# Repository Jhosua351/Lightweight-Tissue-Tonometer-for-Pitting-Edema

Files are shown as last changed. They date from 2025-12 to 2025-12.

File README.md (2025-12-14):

# Lightweight Tissue Tonometer for Detecting Pitting Edema

This repository contains the source code, calibration scripts, and supporting documentation for a capstone project at **Case Western Reserve University**: the design and implementation of a lightweight tissue tonometer device for detecting and classifying **pitting edema**.

---

## Overview
Pitting edema is a clinical symptom characterized by swelling and indentation of tissue due to fluid accumulation. Current diagnostic methods are subjective, relying on visual inspection and manual grading.  
This project introduces the foundation for a future **feedback-controlled tonometer** device that applies a known force and measures tissue displacement, enabling **objective, standardized diagnosis**.

---

## Subsystems
The device integrates three primary subsystems:

- **Force Sensing**  
  - Custom capacitive sensor using penny plates.  
  - FDC1004 capacitance-to-digital converter.  
  - Digital Butterworth low-pass filter for noise reduction.

- **Displacement Sensing**  
  - TCND5000 infrared photodiode sensor.  
  - Exponential low-pass filter for smoothing.  
  - Calibration script converts ADC values to displacement (mm).

- **Pressure Actuation**  
  - Pneumatic bellow system driven by syringe pump.  
  - Designed to apply ~9 N of controlled force.  
  - Displacement range: 6–10 cm.

---
## Repository Contents
- `Sensor-Code/`  
  - `fdc1004_calibration.ino` → Arduino script for force sensor calibration  
  - `tcnd5000_calibration.ino` → Arduino script for displacement sensor calibration  

- `Report/`  
  - `Lightweight Tissue Tonometer For Detecting Pitting Edema Technical Report.pdf` → Final technical report  

- `PCB Files/`  
  - Contains Version 1 and Version 2 PCB layouts and schematics  

- `Capacitive-Force-Sensor-Design/`  
  - Mechanical design files for the capacitive force sensor  

- `Bellow Design/`  
  - `V1/` → First iteration of bellow mold and design  
  - `V2/` → Second iteration with improved flexibility and displacement  

- `Air-Intake-Plus-Clear-Plate-Design/`  
  - Mechanical design of the air intake and clear acrylic plate    

---

## Features
- Sensor calibration with **digital filtering** (Butterworth + exponential smoothing).  
- Conversion of raw ADC values into **voltage and displacement measurements**.  
- Classification of pitting edema into **four clinical grades** based on indentation depth.  
- Debug output for plotting and verification.  

---

## Clinical Grading Scale
| Grade | Indentation Depth |
|-------|------------------|
| 1+    | < 2 mm |
| 2+    | 2–4 mm |
| 3+    | 4–6 mm |
| 4+    | 6–8 mm |

---

## PCB Versions
Two iterations of the printed circuit board (PCB) were developed during the project:

- **Version 1**  
  - Incorporated a motor driver to enable future integration of feedback control.  
  - Layout was less optimized, leading to challenges with signal stability and trace routing.  

- **Version 2**  
  - Motor driver was removed to simplify design and improve tracing.  
  - Enhanced connections for the FDC1004, TCND5000, and supporting components.  
  - More compact and reliable layout.  

Future students should build upon Version 2, but consider further improvements in **shielding** to prepare the design for clinical-grade testing.

---

## Bellow Versions
Multiple versions of the pneumatic bellow were designed and tested:

- **Version 1**  
  - Cast in Dragon Skin 20A silicone rubber.  
  - Wall thickness of 3 mm, triangular folds.  
  - Achieved ~8 mm displacement, below the target of 12 mm.  

- **Version 2**  
  - Reduced wall thickness to 2.5 mm for greater flexibility.  
  - Added a fourth fold to increase expansion area.  
  - Material switched to Silicone Shore 0030 for improved compliance.  
  - Achieved closer to the target displacement range.  

Future students should explore **harder and stiffer silicone materials** to ensure the bellow holds stable under pressure while still achieving the required displacement.

---

## Recommendations for Future Work
- **Electronics**:  
  - Explore PCB miniaturization for wearable applications.    
  - Improve shielding to reduce environmental noise in capacitance measurements.  
  - Investigate a more precise **IR displacement sensor**, since the current TCND5000 loses accuracy beyond ~15 mm.  
    - Note: The sensor begins measuring at ~50 mm due to the combined height of the bellow and acrylic plate, limiting precision.  
  - Improve the **capacitive force sensor design**:  
    - Consider dielectric material between plates.  
    - Add shielding (e.g., enclosing box) to reduce interference from external capacitance sources such as nearby human bodies.
    - Improve shilding on the coaxial wire.  

- **Mechanical Design**:  
  - Refine bellow molds for consistent wall thickness.  
  - Use stiffer silicone materials to improve stability under pressure.
  - Cast a bellow that is black or a darker color to reduce light environmental noise in the IR sensor.   

- **Software**:  
  - Implement closed-loop feedback control for force and displacement.  
  - Add rebound-time measurement to align with full clinical grading standards.    

---

## Getting Started
1. Clone this repository:
   ```bash
   git clone https://github.com/Jhosua351/lightweight-tissue-tonometer.git

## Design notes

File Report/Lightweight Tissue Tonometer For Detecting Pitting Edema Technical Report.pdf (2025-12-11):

### Lightweight Tissue Tonometer Device for Detecting Pitting Edema

Jago Dorn

1,2
(jpd101) Lauren Hong

1
(syh26) Connor Kissack

1
(cak173) Jhosua Oajaca

1,2
(jao101)

Technical Advisor: Dr. Zonghe Chua, Assistant Professor, Department of Electrical, Computer, and Systems Engineering, Case School of Engineering

Instructor: Dr. Vira Chankong

Submitted for ECSE 398 in partial fulfillment for the degree of Bachelor of Science of

Electrical Engineering

1
| Systems & Control Engineering

2

Case Western Reserve University

Fall 2025

### Academic Integrity Policy

All students in this course are expected to adhere to the University standards of academic integrity. Cheating, plagiarism, misrepresentation, and other forms of academic dishonesty will not be tolerated. This includes, but is not limited to, consulting with another person during an exam, turning in written work that was prepared by someone other than you, making minor modifications to the work of someone else and turning it in as your own, or engaging in misrepresentation in seeking a postponement or extension. Ignorance will not be accepted as an excuse. If you are not sure whether something you plan to submit would be considered either cheating or plagiarism, it is your responsibility to ask for clarification. For complete information, please go to https://students.case.edu/community/conduct/aiboard/policy.html.

The individual(s) submitting this document affirm compliance with the above statement

# Lauren Hong Connor Kissack Jhosua Oajaca

[This page intentionally left blank]

### Executive Summary

Pitting edema is a symptom of the accumulation of intercellular fluid in tissue cells that results from an increase in interstitial fluid, characterized by swelling of tissues and formation of an indentation wherever pressure is applied to the skin. While early detection is critical because it indicates underlying heart, liver, or kidney issues, current diagnostic methods are subjective, relying solely on a clinician’s visual assessment and grading of the skin indentation and rebound time. To address the lack of standardization, potential misclassification of severity, and delayed diagnosis, we designed a feedback-controlled tonometer capable of applying a known force and precisely measuring skin displacement and the normal force exerted by the skin on the device. Our methodology integrates three primary subsystems: (1) a capacitive force sensor to measure the force applied to the skin, utilizing two isolated copper plates and a capacitance-to-digital converter (FDC1004) to quantify the normal force; (2) an infrared displacement sensor (TCND5000) to measure the depth of the pit formed; and (3) a pneumatic actuator that uses a syringe pump, motor, and motor driver to regulate the pressure in a silicone bellow to apply constant indentation. We expect the device to apply a controlled force of approximately 10 N and measure skin indentation. We expect the prototype to deliver consistent, precise performance across its subsystems. The device is designed to measure internal actuation displacement over a range of 0–12 mm. Additionally, the device will record and process data sufficient to classify pitting edema into the four standard clinical categories, thereby laying the groundwork for objective, standardized diagnoses.

[This page intentionally left blank]

### Table of Contents

[This page intentionally left blank]

### Problem Statement

Pitting edema is a symptom of the accumulation of intercellular fluid in tissue cells that results from an increase in interstitial fluid, characterized by swelling of tissues and formation of an indentation wherever pressure is applied to the skin. While early detection is critical because it indicates underlying heart, liver, or kidney issues, current diagnostic methods are subjective, relying solely on a clinician’s visual assessment and grading of the skin indentation and rebound time. To address the lack of standardization, potential misclassification of severity, and delayed diagnosis, we designed a tonometer capable of applying a force and precisely measuring skin displacement and the normal force exerted by the skin on the device. This system would allow either healthcare professionals or researchers to collect data, helping them create a validated grading system. Future iterations of this system could also allow patients to measure the extent of their pitting edema, encouraging timely care-seeking behaviors that could support early diagnosis or better chronic disease management.

The overall goal of this project is to design a fully functional tonometer device that applies and measures force and displacement by pressing into the patient’s tissue (typically on the forearm or calf), serving as a proof-of-concept design to provide clinicians with reliable, objective measurements to support the diagnosis and monitoring of pitting edema. To achieve this, we will design and implement subsystems for force sensing, displacement sensing, and actuation/pressurization.

A relatively long search for relevant studies and papers returned no devices that used similar methods to measure pitting edema. The most relevant paper we found was “Quantitative measurement of pitting edema with a novel edema ruler” [1], in which the team designed and 3D-printed a handheld tool to measure the depth of a pit created by manually applied pressure, which could then be used to help physicians in subjectively deciding an edema grade level for the patient. There has been some discussion of the lack of standardization in grading pitting edema [2], suggesting a common interest in a solution like the one we designed in our project. Similar circulatory issues can be detected with the peripheral arterial tonometry, a non-invasive test that assesses circulation by measuring changes in blood flow and arterial function [3]. This shows that using objective, sensor-based measurements has already improved the diagnosis of related issues, highlighting how our tonometer could help make edema assessments more consistent.

### Purpose, Goals, & Objectives

The purpose of this project is to develop a prototype diagnostic tonometer device that applies force to the skin at various body locations to measure tissue displacement and objectively assess the severity of pitting edema. With this device, clinicians would be able to quantify the applied force and the resulting tissue displacement, thereby standardizing the diagnostic method for edema.

This project supports the organizational objectives of creating a standardized diagnostic method to improve accuracy and consistency, and of creating a final wearable device ready for marketing to clinicians and, in the future, patients who want to self-assess at home. The business problem being addressed is the potential delay in diagnosis, which could lead to misclassification of disease severity and, in turn, increase care costs. This project has a high priority because this device can improve both clinical decision-making and self-monitoring for at-risk patients at home. In the long term, this device can improve chronic disease management and support preventive and remote monitoring.

The three main aspects of the project that are necessary to support the desired functionalities are
(1) force sensing, (2) displacement sensing, and (3) pressure actuation. The force sensor records force data that may help researchers determine whether the amount of force applied is a variable that can guide methods for grading pitting edema. It also helps as a safety measure by creating a stopping point for the applied pressure, ensuring that reasonable pressure is applied so the patient does not get hurt. In future developments of this device, the force sensor will help create a feedback control system that applies the force needed to maintain constant tissue displacement, thereby helping determine the normal force exerted by the skin on the device. The displacement sensor measures the amount of tissue displacement created by the device's applied force, which is the main functionality of our device. The pressure actuation subsystem generates the pressure that induces indentation in the patient’s skin.

Dr. Chua’s team aims to develop a wearable device that precisely measures and categorizes pitting edema with minimal involvement from healthcare professionals. Before beginning our project, the device was at a Tech Readiness level of two (“Technology Conceptualized”) [4], with a timeline of 5 to 7 years before it could be implemented in a healthcare setting. Our project team aimed to demonstrate key elements in a laboratory environment that would indicate progression to a Tech Readiness level four (“Partial Scale Prototype & Modeling”) [4]. Our project is a prototype subsystem that will provide foundational data and establish a developmental framework for Dr. Chua’s team.

### Background & Context

Pitting edema is usually checked using a pretty straightforward method: a doctor presses a finger into the patient’s skin, usually on the forearm or calf, and watches how deep the dent goes and how long it takes for the skin to bounce back. This “finger method” [5] is standard, but it is pretty subjective, meaning it depends heavily on the doctor's opinion of how bottomless the pit is and how quickly it rebounds. Because of this, different practitioners can end up grading it inconsistently, which can slow down the diagnosis of serious issues like heart problems, kidney trouble, or liver disease.

To address this inconsistency, researchers have explored more precise methods. One notable innovation is the edema ruler [1], a small device made to measure the depth of the pit more accurately. While the ruler gives a specific number for the indentation's depth, it still relies on manual pressure and does not account for how quickly the skin rebounds or how evenly the pressure is applied. So, even though it is a step forward in accuracy compared to the finger method, it is not perfect for eliminating variability in assessment.

In practice, pitting edema is typically classified into four standard grades based on how deep the indentation is:

Table 1 - Pitting Edema Grade Scale [7]

Grade | Indentation Depth | Rebound Time
1+ | < 2 mm | Immediately
2+ | 2 - 4 mm | < 15 seconds
3+ | 4 - 6 mm | < 60 seconds
4+ | 6 - 8 mm | 2 − 3 minutes

While rebound time is important for identifying and classifying pitting, it was out of scope for this project. We hope that, with future updates using feedback-controlled actuation, we can add a rebound time to create a more rounded diagnostic tool.

By placing our work alongside existing diagnostic methods (such as the finger method and the edema ruler), the clinical grading standards, and the technical challenges of sensor development, this project shows both the need for and the potential of a standardized, quantitative tonometer for assessing pitting edema.

### Success Criteria

The project will be a success if the following criteria are met or exceeded:
- The device can measure internal actuation displacement with an uncertainty of ±1 millimeter.
- The device can measure force at the end effector with an uncertainty of 10%.
- The device end-effector can detect contact with human skin within 0.5 seconds, with at least 1 newton of force applied.

- The device can extend and retract the end effector by at least 8mm at a frequency of at least 0.25 Hz.
- The device can record and share data that enables the classification of pitting edema into the four categories. The categories are defined by the pit depth: < 2 mm, 2-4mm, 4-6mm, and > 6 mm [7].
- The device complies with the standards listed below.

The constraint of measuring internal actuation displacement with an uncertainty of ±1 millimeter is most impactful to our device design, as it is our primary means of measuring pitting edema. In the most severe cases, pitting edema may produce depressions of around 8 millimeters, meaning that even small measurement errors could alter the assigned edema grade. Achieving ±1 millimeter uncertainty constrains the selection of sensors, mechanical tolerances of the pressure actuation subsystem, and the stiffness of the different materials used (silicone of the bellow, flexures of force capacitors, etc). It also influences the calibration process, necessitating the removal of noise or drift so that the measurements reflect close to true tissue indentation. This success criterion drove both mechanical and electrical design decisions and ultimately ensured the clinical meaningfulness of the device.

The constraint of measuring force with an uncertainty of 10% at the end effector is also meaningful to our device design, as it records the load applied to the skin, providing researchers with data that may show whether the applied force is a reliable parameter for guiding clinical grading pitting edema. It also functions as a safety mechanism by defining an upper limit on applied pressure, ensuring the device cannot exert excessive force that may cause patient discomfort or injury. This is one necessary part for future FDA approvals, as safety is a priority. In future iterations, accurate force measurement will be essential for implementing a closed-loop feedback controller that can modulate the actuation pressure to maintain a constant tissue displacement. This will allow the system to determine the normal force exerted by the skin against the device, another key parameter of interest. Because force interacts directly with the displacement-sensing and pressure-actuation subsystems, a 10% uncertainty constraint places strict requirements on sensor selection, mechanical design of the capacitor, and calibration, ensuring that the measured force reflects close to the true applied force and normal force rather than system noise or environmental noise.

The success criteria that the device should extend and retract the end effector by at least 8 millimeters at a minimum frequency of 0.25 Hz directly influences the design of the pressure-actuation subsystem. Because displacement is our primary measurement, the actuator must be capable of producing sufficient stroke length to replicate the full range of clinically relevant pitting-edema levels of depth. Meeting this displacement requirement ensures that we can reliably induce measurable pits across the full spectrum of edema severity. The frequency requirement of 0.25 Hz also constraints the performance of the actuator so that the system can complete a full indentation-release cycle every four seconds. These constraints affect the selection of the actuation mechanism, the stiffness and response characteristics of the bellow, and the sizing and control strategy of the pneumatic subsystem. They also shape the decisions in making the overall mechanical design to ensure repeatable motion and minimal latency.

### Technical Constraints

The accuracy of the force and displacement sensing portions of the device must remain within clinically acceptable tolerances, as the differences in displacement and force pushback from the skin are minute, and the degrees of pitting edema can differ by tiny increments. To provide meaningful diagnostic value, we must balance cost and sensor precision, and place strict requirements on sensor selection and calibration methods.

Another constraint during the prototype phase is size. To mimic current manual depression methods on the patient’s skin, the device needs a pressure tip no larger than a thumb, or about 2 cm in diameter. The rest of the device needs to be compact enough to be made into a wearable device that securely fits on a person’s limbs. Future iterations will need to consider shrinking the device to meet the size specifications required to make this into a wearable device.

Safety constraints should also be considered, as we want to ensure that safety restrictions are in place to prevent excessive pressure on the patient.

### Standards

Our project will follow a set of standards to make sure the device is safe, reliable, and easy to integrate with other systems. On the regulatory side, we’ll meet the FCC requirements under Title 47, Part 15 (Sections 15.23 and 15.5), which cover electronic emissions and interference. For the hardware, we’ll use IEC 60320-1 for electrical connections and IPC-2221B for printed circuit board design (PCB). For communication, we’ll rely on IEEE 1118.1-1990 for microcontroller control buses and the I2C protocol to handle data transfer between subsystems. Since this is a medical-focused project, we’ll also reference ISO/IEEE 11073 standards to keep our device aligned with healthcare communication practices and patient safety.

1) Generic Standard on Printed Board Design, IPC-2221B, IPC, Bannockburn, IL, 2012. [Online]. Available: IPC_2221.pdf (https://www-eng.lbl.gov/~shuman/NEXT/CURRENT_DESIGN/TP/MATERIALS/IPC_2221.pdf)

IPC-2221B, Generic Standard on Printed Board Design, is an industry standard published by IPC that provides the design principles and requirements for printed circuit boards (PCBs). It covers material selection, conductor spacing, thermal management, mechanical layout, and electrical performance considerations. Its purpose is to ensure manufacturability and safety across PCB applications by establishing design rules that can be adapted to different technologies.

1) Radio Frequency Devices, Title 47 CFR Part 15, Federal Communications Commission,
Washington, | D.C., | 2023. | [Online]. | Available:
https://www.ecfr.gov/current/title-47/part-15

Under Title 47, Part 15 of the FCC rules, Section 15.23 allows individuals to build and operate low-power radio frequency devices for personal use without formal equipment authorization. Provided no more than five units are made, and they do not cause harmful interference. Section 15.5 sets out the operating conditions for all Part 15 devices. They must not cause harmful interference to licensed radio services, must accept any interference received, and must stop if ordered by the FCC.

2) Universal Serial Bus Type-C Cable and Connector Specification, Release 2.4, USB 3.0
Promoter | Group, | Oct. | 2024. | [Online]. | Available:
https://www.usb.org/document-library/usb-type-cr-cable-and-connector-specification-rele ase-24 (https://www.usb.org/document-library/usb-type-cr-cable-and-connector-specification-release-24)

The USB Type-C Cable and Connector Specification Release 2.4 provides the newest framework for ensuring safety performance across devices that adopt the standard. This release refines definitions for cable assemblies, connector requirements, and extended power delivery. It introduces updated compliance requirements for USB4 Gen4 and liquid corrosion mitigation and alternate modes. For engineers and system designers, this serves as a reference for implementing Type-C technology in devices.

3) IEEE Standard for Microcontroller System Bus, IEEE Standard 1118.1-1990, 1990. [Online]. Available: https://ieeexplore.ieee.org/document/159173

The IEEE 1118.1-1990 standard defines the specifications for microcontroller control buses, providing a uniform method for communication between microcontrollers and peripheral devices. It establishes electrical, timing, and protocol requirements for data transfer, device interoperability, and control in embedded systems. By standardizing bus operations, IEEE 1118.1-1990 helps reduce design complexity, promotes hardware compatibility, and supports scalable system development.

4) Solderability Tests for Component Leads, Terminations, Lugs, Terminals and Wires, Joint standard, EIA/IPC/JEDEC J-STD-002E, IPC, EIA, and JEDEC, Nov. 2017. [Online]. Available:https://webstore.ansi.org/preview-pages/ipc/preview_j-std-002e.pdf?srsltid=AfmBOopS_s9edY3xJrSCdWhQsNor4nRz5zq07qOXc5j1KHITtFKT7D1X (https://webstore.ansi.org/preview-pages/ipc/preview_j-std-002e.pdf)

The J-STD-002E standard provides a methodology for evaluating the solderability of component leads and wires used in electronic assemblies. It establishes visual criteria and force measurement tests. These procedures verify the components maintain acceptable solderability throughout storage and assembly. The standard helps suppliers and users ensure long-term reliability.

5) Reference Designations for Electrical and Electronics Parts and Equipment, ASME Y14.44-2008, The American Society of Mechanical Engineers, Nov. 21, 2008. [Online]. Available:
https://www.intertekinform.com/preview/98393739772.pdf?sku=138813_SAIG_ASME_ASME_2631634&srsltid=AfmBOoqN_DQIZ4u7QUdkdc9FvU-_kXyi-eiCwLqGUh5Ni5 6hMhtX3eZU (https://www.intertekinform.com/preview/98393739772.pdf?sku=138813_SAIG_ASME_ASME_2631634)

This defines a uniform system for reference applied to electronic equipment. It specifies methods for unit numbering so that components are identifiable in documentation. Y14.44 reduces ambiguity in system layouts and supports manufacturing teams.

6) IPC-A-610E: Acceptability of Electronic Assemblies, IPC – Association Connecting
Electronics | Industries, | Apr. | 2010. | [Online]. | Available:
https://datasheet.datasheetarchive.com/originals/crawler/acdi.com/4fa15157e5b81fef1873 e725a900d3e8.pdf (https://datasheet.datasheetarchive.com/originals/crawler/acdi.com/4fa15157e5b81fef1873e725a900d3e8.pdf)

The standard provides criteria for the inspection and quality evaluation of electronic assemblies. It establishes classifications for assemblies. Class 1: general electronic products, Class 2: dedicated service, and Class 3: high-performance.

### Approach & Design Methodology

Our approach uses three main subsystems: Force sensing, displacement sensing, and pressure actuation. We chose this path because it strikes a balance among accuracy, safety, and practicality, while also building on methods that are more reliable than current clinical evaluations.

We felt this was the best direction compared to existing options, such as simple mechanical tonometers, which aren’t very accurate and depend heavily on the clinician. Our approach enables more objective and repeatable results, setting the stage for future improvements to wearable devices.

Force Sensing

While working on our prototype, we ran into familiar measurement issues. At first, we considered using a standard resistive force sensor, but they are often inaccurate, prone to drift, and challenging to customize. To tackle these problems, we decided to design and build our own capacitive force sensor. Since we were on a tight budget, we used two copper pennies from before 1982 as the capacitor plates. While this worked, it came with its own set of challenges: pennies are less conductive than aluminum and are more affected by environmental noise. With a larger budget, we would have substituted the pennies for slices of aluminum rods for the capacitor plates to improve conductivity and reduce sensitivity to noise.

We designed our capacitor using two isolated copper plates. These have a capacitance between them that can be measured using a capacitive-to-digital chip. The plates are mounted on a flexure that compresses when force is applied. These plates were sized appropriately and fixed at a 1.5 mm distance to ensure the reading of a maximum capacitance of 15 pF when applying a maximum force of 10 N. This was done to ensure that the applied force remained within the FDC1004's range, a four-channel capacitive-to-digital converter.

Calibration was another big hurdle. The capacitive sensor was picking up significant external noise, so we implemented a digital low-pass filter, or specifically a first-order Butterworth low-pass filter, to smooth the signal and remove noise.

This filter is defined by its discrete-time transfer function H[z] = | , where | is the

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
−1 ] + ω0

ω0

cutoff frequency and T is the sampling period. And the corresponding difference equation we
s
used to implement this filter is y[k] = ( | | .

2−ω0

T
s
2+ω0

Ts

)y[k − 1] +

ω0

T
s
2+ω0

Ts

x[k] +

| ω0 T s 2+ω0 Ts
x[k − 1]

Even with filtering, some readings were too weak to be useful, so we added an amplifier to boost the signal into a measurable range. While calibrating, we also realized that the flexure holding the pennies was flawed in that the flexure would not rebound fully over time, causing drift in our capacitance measurements. These steps were essential for meeting our accuracy goals, but they really highlight how tough it can be to build reliable biomedical sensors when resources are limited.

Displacement Sensing

To measure skin response, we used a photodiode displacement sensor. This sensor will help us track how far the skin is displaced. This works by measuring the internal displacement of the bellow through emitting and detecting infrared light. By measuring the current generated by the photodiode, we can determine how close the opposite side of the bellow is to the sensor. We chose this method due to its low cost, precision, and ease of integration compared to more bulky or less accurate alternatives.

Pressure Actuation

For the actuation subsystem, we developed a pneumatic bellow to apply controlled pressure in the y-direction. Our first version was inspired by a Soft Robotics project that focused on pneumatic actuators, which we used as a guide for designing the mold and its shape [6]. We made a two-piece mold for the bellow, keeping three main things in mind: wall thickness, folding angle, and fold shape.

For wall thickness, we went with 3 mm after reviewing a research paper on soft-bellow actuators [7]. At 50 kPa, this thickness yielded the best deformation, with a displacement of 14.58 mm. In contrast, a six mm-thick option only provided 5.49 mm of movement [7]. While the original actuator was for a different purpose, the design and pressure factors still worked for what we were trying to do.

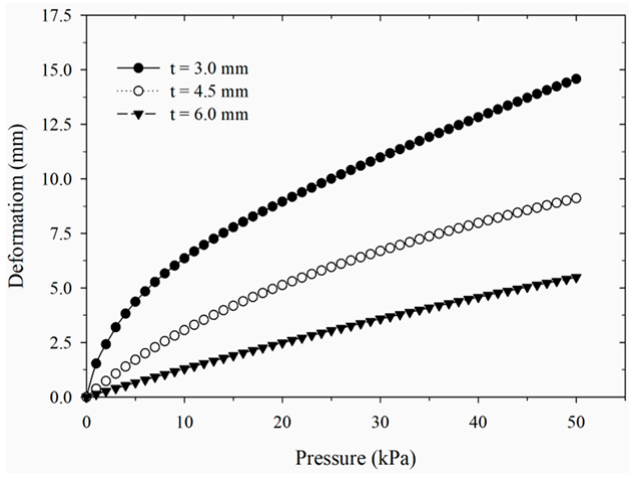
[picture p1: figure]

Figure 1: Simulation result of deformation response under 50 kPa pressure with wall thickness of 3mm [7]

We chose a folding angle of 30° based on the techniques described in the paper on soft bellow actuators and on Dr. Chua’s previous work with mechanical bellow designs [8]. For the fold shapes, we kept it simple with triangular designs, following the guidelines from the Soft Robotics project [7].

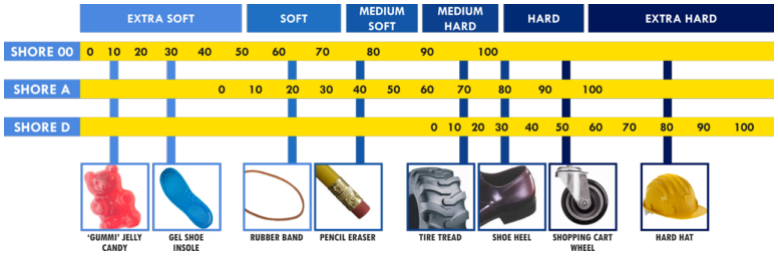
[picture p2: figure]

Figure 2: Silicon Shore Hardness Scales [9]

For the materials, we cast the bellow in Dragon Skin 20A silicone rubber. This was a good choice because it is as flexible as a rubber band, and we thought it would let the bellow expand up to 12 mm, which was our goal. We also used epoxy glue made for silicone to stick the two halves together since we cast it in two parts.

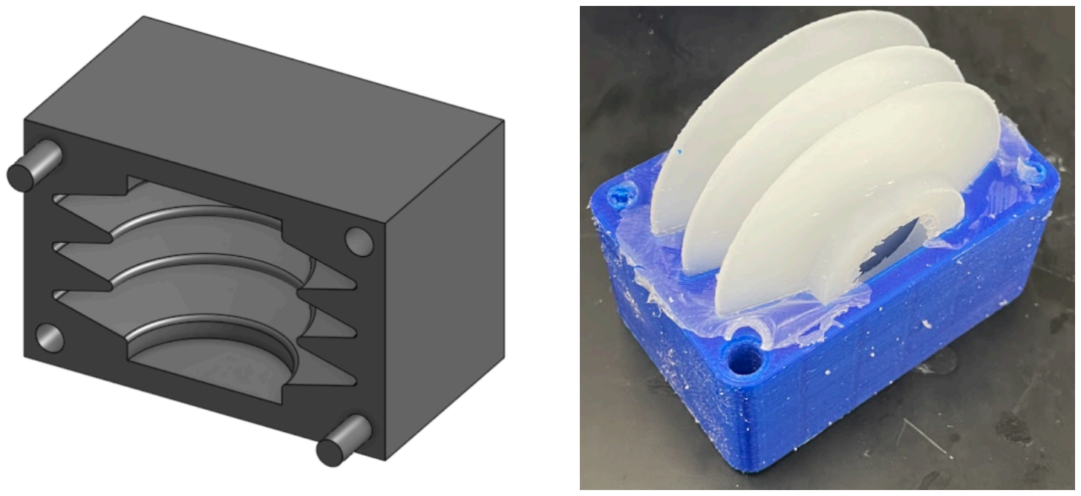
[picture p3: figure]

Figure 3 - Bellow Mold and Cast

Testing it with a syringe showed that our first design did not quite reach the target of 12 mm, expanding only to 8 mm. To fix that, we created a second design with some changes: we added a fourth fold to increase the expansion area, reduced the wall thickness from 3 mm to 2.5 mm for greater flexibility, and switched the material from Dragon Skin 20A to Silicone Shore 0030 for even greater compliance. These tweaks improved the actuator’s performance and helped it get closer to meeting our displacement goals.

Physical Device

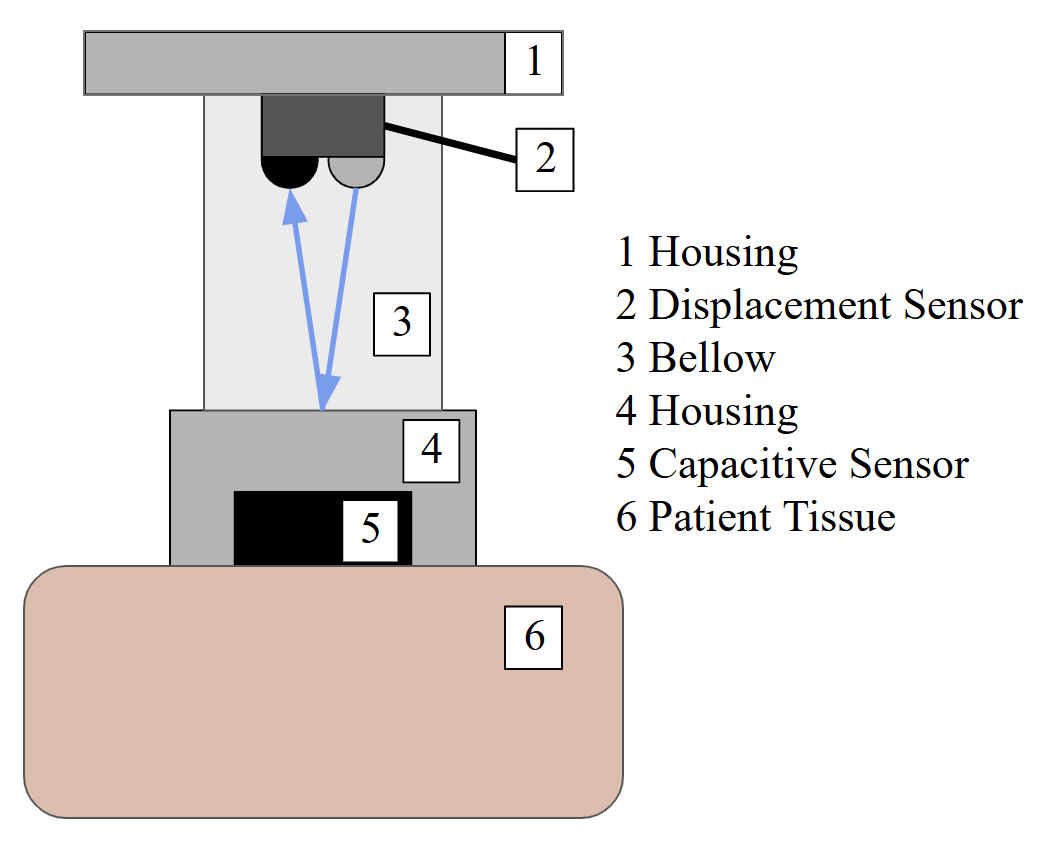
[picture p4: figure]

Figure 4: Hardware Design Overview

Figure 4 shows the design overview and how the device is supposed to work. As the bellow is inflated, the distance between the housings will increase, and this will be read using an infrared emitter and detector sensor circuit. The force of the patient’s tissue against the device will be measured using the capacitive sensor. This way, we can determine whether we are in contact with the patient, whether the tissue is responding in a way consistent with edema, and how deep the tissue has been displaced.

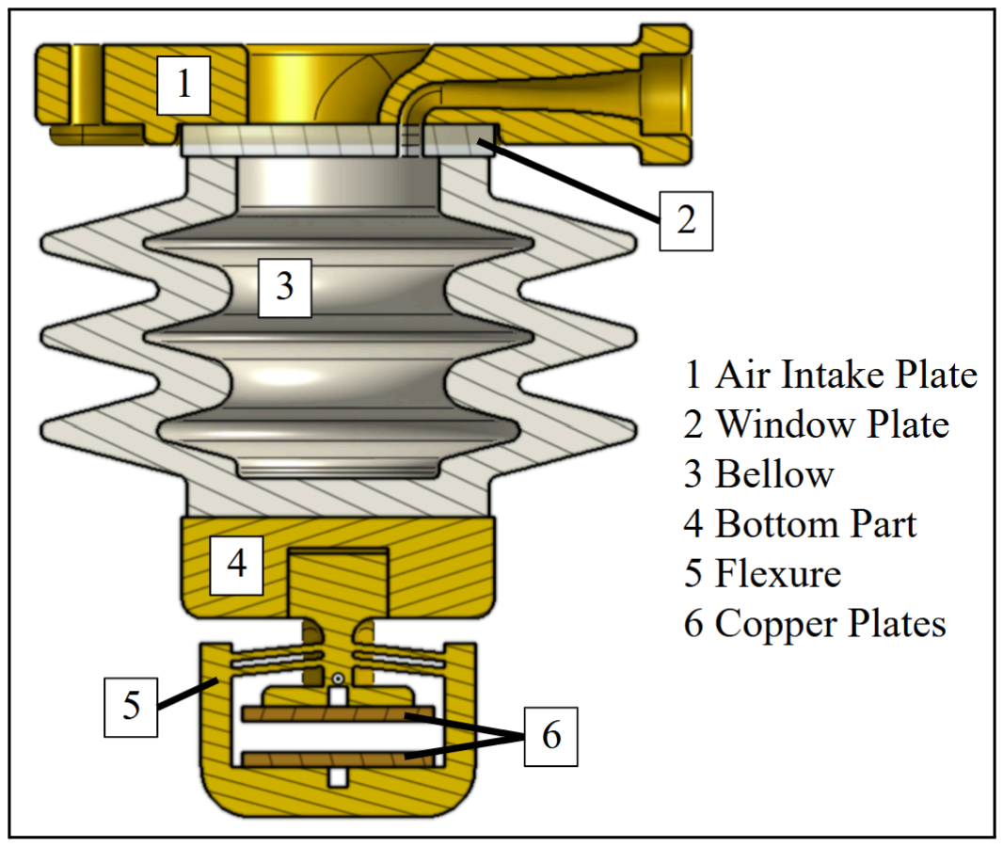
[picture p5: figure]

Figure 5: Physical Computer-Aided Design

The physical design consists mainly of the components listed above. This is in addition to the printed circuit board mounted on the air intake plate, several wires, and the air intake hose. This design was created in Onshape, a computer-aided design (CAD) software.

Circuit Design

Schematics for the displacement sensor, capacitance sensor, and ESP32 pinout and connections were all designed in KiCAD, a circuit design software. Then, these schematics were combined and translated into a printed circuit board layout in KiCAD. The printed circuit board was designed to implement shielding for our capacitive sensor, mitigate environmental noise with two-layer ground fills, and parallel traces to reduce crosstalk.

Alternative Designs

Both the physical and circuit designs had multiple iterations. Shown below are some iterations for each component.

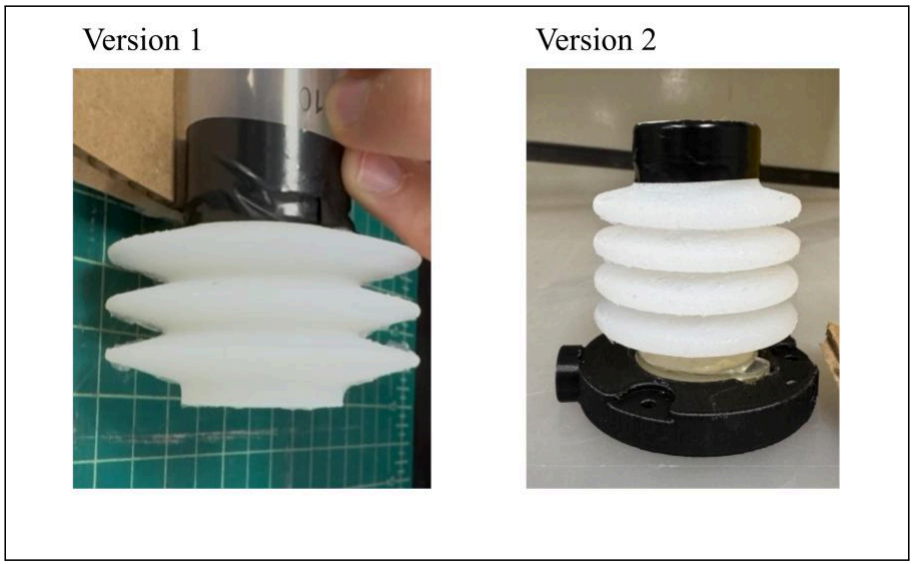
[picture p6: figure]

Figure 6: Bellow Iterations

Bellow version 1 did not have adequate extension when inflated. For this reason, and to create a thicker wall for better adhesion to the top and bottom fixtures, version 2 was created.

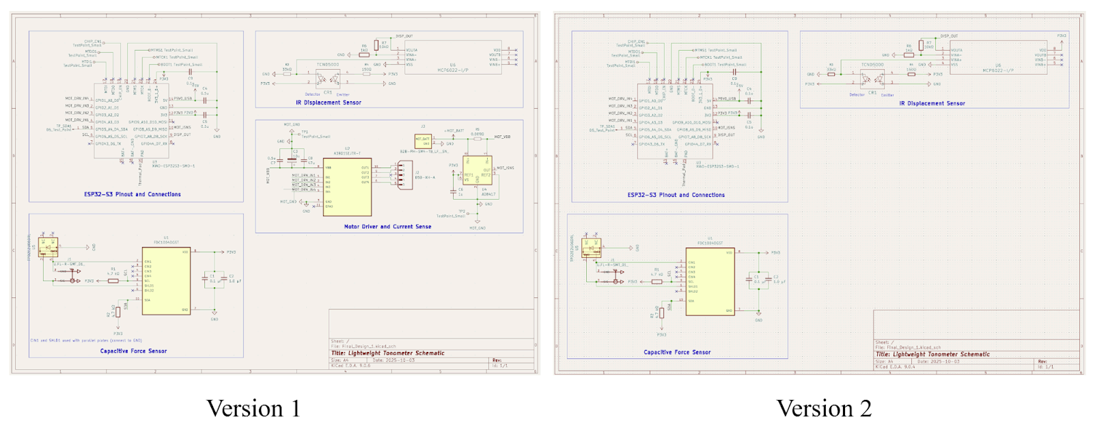
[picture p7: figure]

Figure 7: Schematic Iterations

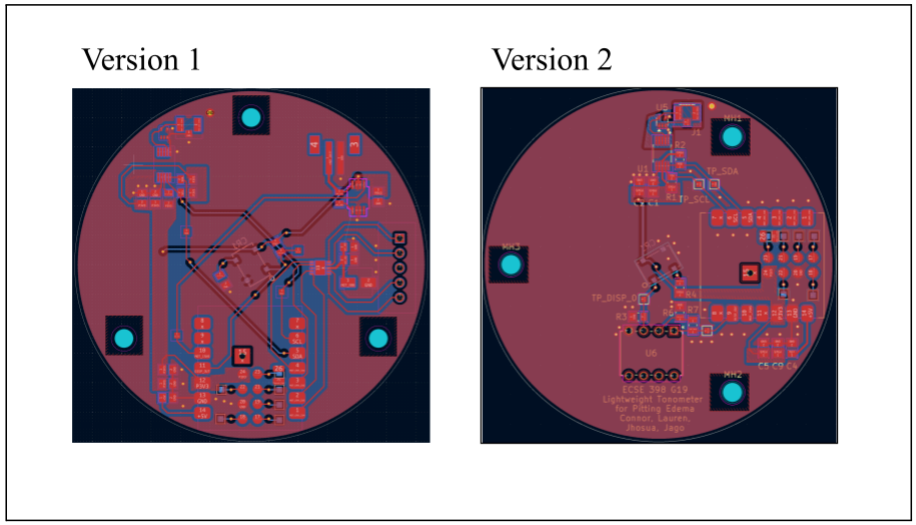
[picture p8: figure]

Figure 7: PCB Iterations

After testing our first PCB, we determined that the displacement sensor did not vary enough to provide accurate data and was highly susceptible to external noise. After troubleshooting and experimentation, we found a solution, implemented it in our second schematic version, and then updated the PCB design. In addition, we removed the current-sense feature and motor-driver connectors, which were used when the project had a broader scope. We also widened the driving-voltage traces and added a through-hole for an operational amplifier to increase gain in the displacement sensor’s output. As a precaution, we also redesigned the capacitance force sensor circuitry to improve I2C connectivity by shortening the SDA and SCL traces, making them as parallel as possible, and ensuring there were no breaks in the ground plane beneath the traces and pins.

By combining these subsystems, we designed a proof-of-concept device that integrates force sensing, displacement measurement, and pneumatic actuation into a single system.

### Verification & Results

Our first criterion was to ensure that our device measures internal actuation displacement with an uncertainty of ±1 millimeter. This was established using the TCND5000 IR sensor, implementing a first-order, digital low-pass Butterworth filter and a moving average function to reduce noise, situating our IR sensor perpendicular to a wall, and using a caliper to corroborate distances to voltage readings with the sensor. As a result, we decided to set the cutoff frequency 10 Hz, the sampling period 0.01 seconds per sample, and averaged over 50 samples. From the difference equation and these values, we obtained coefficients a = 0. 7285 and b = 0. 1358. In doing so, we uncovered a non-linear relationship between these two readings and obtained a fourth-order polynomial function that fit our data. From this fit, we obtained a minimum standard error of 0.0 mm, a maximum standard error of 0.7 mm, and an average standard error of 0.3167 mm, which met our 1 mm uncertainty criterion.

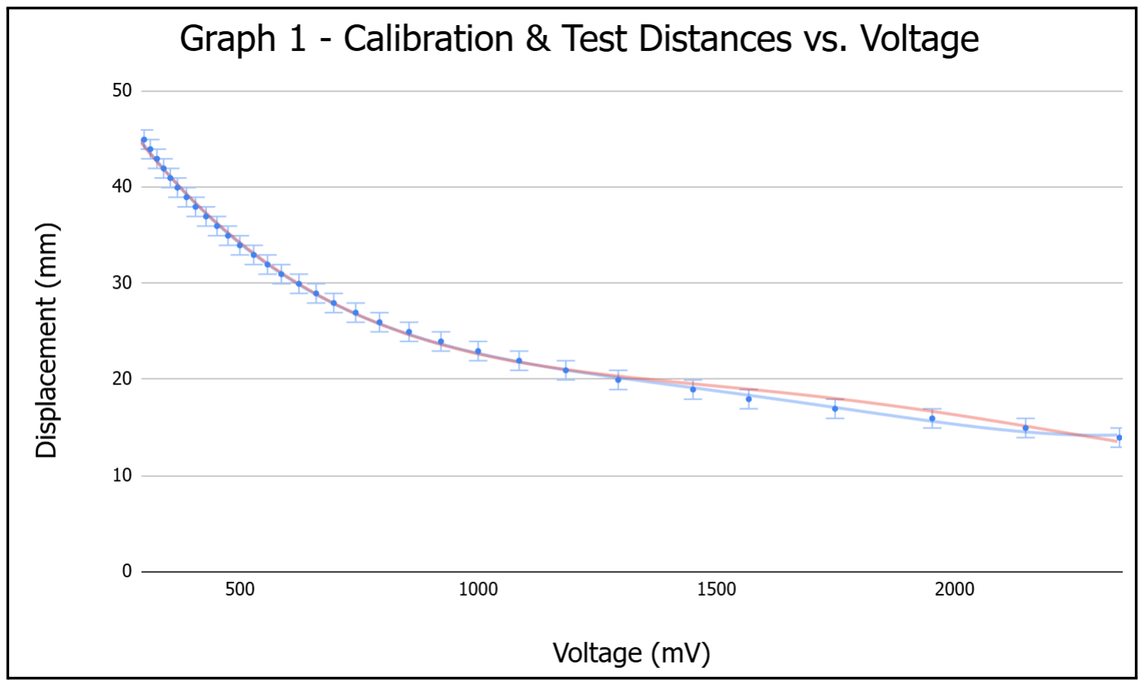
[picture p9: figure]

Figure 8: Graph of Calibration (Blue) and Test (Red) Distances with Voltage

Our second criterion was to ensure the device measures force with the end effector within 10% uncertainty. Under the right conditions, we were able to obtain measurements with an uncertainty of 10%. This was done by using two copper plates mounted within a flexure, with calibration weights placed directly on top of the flexure, which was mounted perpendicular to the surface. However, environmental interference and minor flaws in our flexure's mechanical design hindered our ability to corroborate capacitance readings with the applied weight consistently. We also implemented the same first-order, low-pass digital Butterworth filter, combined with a moving average, to reduce interference and noise. Although we were able to reduce most of the noise, the sensor’s sensitivity still caused environmental interference in our readings. This could be improved by incorporating additional shielding, adding a dielectric material, fully enclosing the capacitors, and creating a more robust flexure design to reduce environmental noise as much as possible.

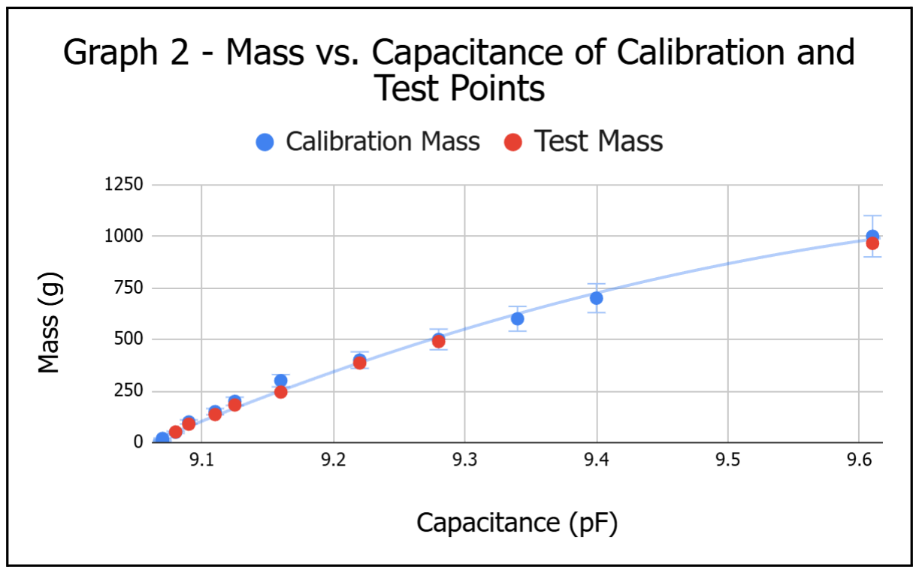
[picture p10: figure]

Figure 9: Graph of Calibration and Test Masses with Capacitance

Our third criterion was to ensure the device’s end effector could detect contact with human skin within 0.5 seconds with at least 1 N of force applied. Using our calibration weights and I2C communication with our ESP32, we consistently obtained force measurements from 1 N to 10 N in under 0.5 seconds. Thus, we met this criterion.

Our fourth criterion was to ensure that the device extends and retracts the end effector by at least 8mm at a frequency of at least 0.25 Hz. This was met, as we obtained about 35 mm of extension and retraction at about 0.4 Hz. This was measured by recording a video of the bellow being extended and retracted next to a ruler, with a timer in the background, so that the extension amount and the frequency of each extension and retraction cycle could be determined from the video playback.

Our fifth criterion was to ensure the device records and shares accurate data to classify pitting edema into the four categories or specified grade levels. To do so, we relied on the TCND5000, our IR displacement sensor. From corroborating measured displacement and the actual displacement associated with the specified grade level, we met this criterion. Figure 10 below depicts how our measurements align with the categorized grade levels, indicating a high success rate. The reason our third measurement is not correct is that it falls between grades 1 and 2 and differs by approximately 0.1 mm. However, this was not the case for other borderlines.

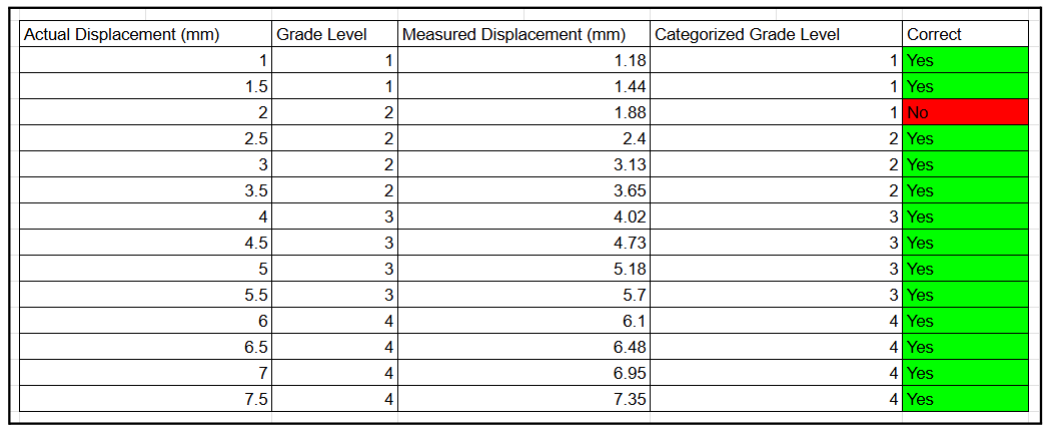
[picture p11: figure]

Figure 10: Table of Actual Displacement Measurements and Categorized Grade Level

Lastly, our sixth criterion was to meet our necessary standards. From the completion of this project, we fully met each standard. That is, FCC requirements under Title 47, Part 15 (Sections 15.23 and 15.5), IEC 60320-1, IPC-2221B, IEEE 1118.1-1990, ISO/IEEE 11073, J-STD-002E, and IPC-A-610E.

### Project Management

We used a Gantt chart to assign and track tasks throughout the project. The Gantt chart below shows task categories, task numbers with their respective milestones, task predecessors, specific task leaders and members, and the duration of each task throughout the project timeline. Figure 11 shows a Gantt chart. Additionally, Dr. Chua assigned us a $100 budget for this project.

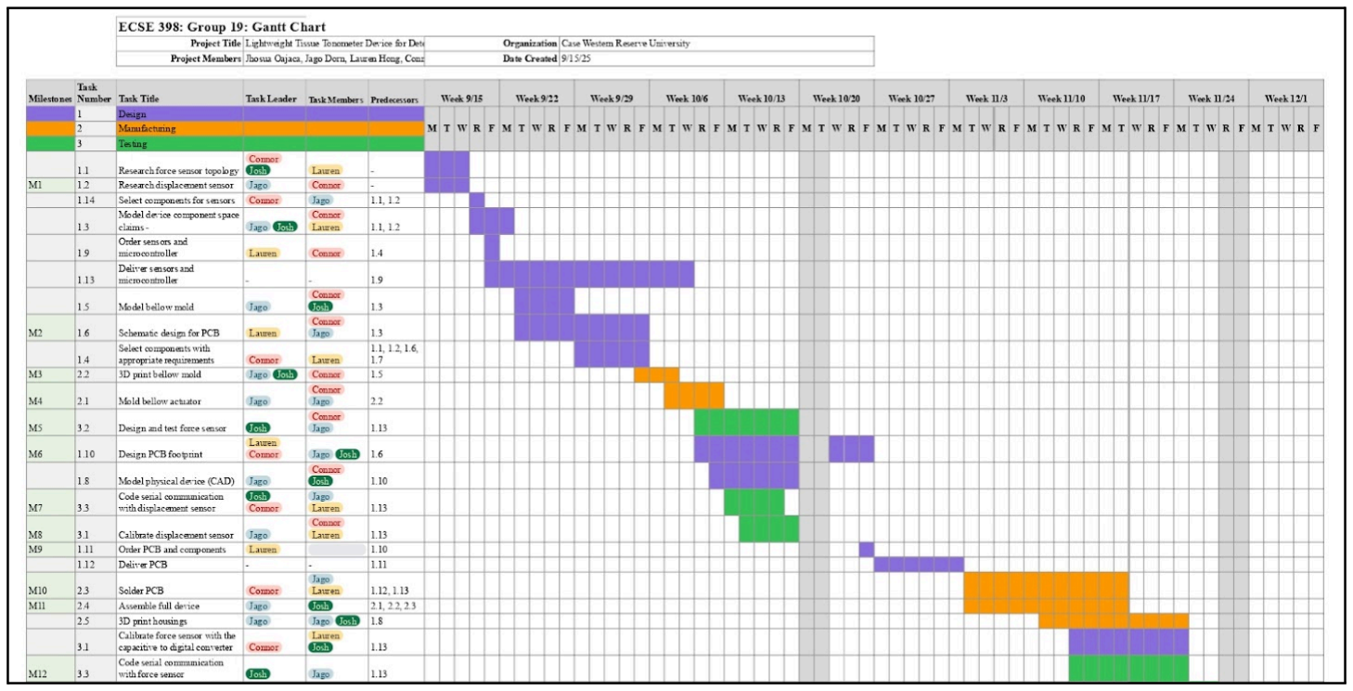
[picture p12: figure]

Figure 11: Gantt Chart for Project Management

### Relevant Courses

Table 1: Relevant Courses with Listed Group Members and Description of Course Relevance
Course | Taken By | Description
ENGR 210 | Jago Dorn, Jhosua Oajaca, Lauren Hong, Connor Kissack | ● Circuit analysis ● Electrical power ● Operational Amplifiers
ECSE 245 | Jago Dorn, Jhosua Oajaca, Connor Kissack | ● Additional complex circuit analysis with diodes ● Spice software
ECSE 395 | Jhosua Oajaca | ● Project management ● Identifying technical constraints
ECSE 326 | Jago Dorn | ● Capacitive and optical design ● Noise filtering ● Analog to digital signal conversion
ECSE 313 / EBME 309 | Jago Dorn, Jhosua Oajaca, Connor Kissack / Lauren Hong | ● Digital Butterworth filter implementation ● Laplace transforms ● Frequency filtering
ECSE 344 | Connor Kissack | ● Implementation and design of real-world circuits under physical constraints
ECSE 488 | Lauren Hong | ● Arduino IDE ● Embedded systems design ● IR sensors ● Project management
ECSE 309 | Jhosua Oajaca, Connor Kissack, Lauren Hong | ● Understanding and physical properties of capacitors

### Appendix A - Arduino Code for Calibration of FDC1004 and TCND5000

/*********** Combined FDC1004 + TCND5000 **********/
#include <Wire.h>

#include <FDC1004.h>

/* ---------------- FDC1004 Setup ---------------- */ const int SDA_PIN = SDA; // GPIO5 = SDA on XIAO ESP32S3 const int SCL_PIN = SCL; // GPIO6 = SCL on XIAO ESP32S3

// Digital Low Pass Butterworth Filter for FDC
float yk1 = 0; // y[k-1]
float xk1 = 0; // x[k-1]
const float a = 0.72848950367272; // cutoff = 10 Hz const float b = 0.13575752481636; // sampling = 100 S/s FDC1004 fdc(FDC1004_100HZ);

/* ---------------- TCND5000 Setup ---------------- */ const int DISP_OUT = A8;

// Low pass filter parameters
float r = 30000;
float c = 0.000000483;
float sample_period = 0.01;
float cutOff_frequency = 1 / (2 * PI * r * c);
float sampling_rate = 1 / sample_period;
float smoothing_factor = expf(-2 * PI * cutOff_frequency / sampling_rate); float filteredValue = 0.0;

/* ---------------- Arduino Setup ---------------- */
void setup() {

Serial.begin(115200);
// Initialize I2C for FDC1004 Wire.begin(SDA_PIN, SCL_PIN); Wire.setClock(100000); // 100 kHz I2C
delay(50);
Serial.println("FDC1004 ready (Wire initialized).");

// Initialize TCND5000 pin
pinMode(DISP_OUT, INPUT);
Serial.println("TCND5000 ready.");
}

/* ---------------- Arduino Loop ---------------- */ void loop() {
/*********** FDC1004 Reading ***********/
float c_fF = fdc.getCapacitance(0); // read CIN1
float pf = c_fF / 1000.0; | // convert to pF

// Butterworth filter
float yk_c = a * yk1 + b * pf + b * xk1;

Serial.print("FDC1004: "); Serial.println(yk_c, 2);

xk1 = pf;
yk1 = yk_c;

/*********** TCND5000 Reading ***********/ int samples = 50;
float total = 0.0;

for (int i = 0; i < samples; i++) {
float raw = analogRead(DISP_OUT);
filteredValue = (1.0f - smoothing_factor) * raw + smoothing_factor * filteredValue;
total += filteredValue;
delayMicroseconds(100);
}
float average = total / samples;
float voltage_mV = (average / 4095.0) * 3300.0;
double displacement = 70 - 0.112 * voltage_mV + 1.01e-4 * voltage_mV * voltage_mV - 4.22e-8 * voltage_mV * voltage_mV * voltage_mV + 6.54e-12 * voltage_mV * voltage_mV * voltage_mV * voltage_mV;

Serial.print("TCND5000 displacement = "); Serial.println(displacement);
if (displacement < 2) {
Serial.println("Grade level: 1");
} else if (displacement < 4) { Serial.println("Grade level: 2"); } else if (displacement < 6) { Serial.println("Grade level: 3"); } else if (displacement < 8) { Serial.println("Grade level: 4");
}
// Example combined CSV-style output for plotting Serial.print("PlotData: ");
Serial.print(yk_c, 2); // capacitance (pF) Serial.print(", ");
Serial.println(voltage_mV); // displacement voltage (mV) delay(10); // small delay before next loop
}

### Appendix B: Circuit Schematics

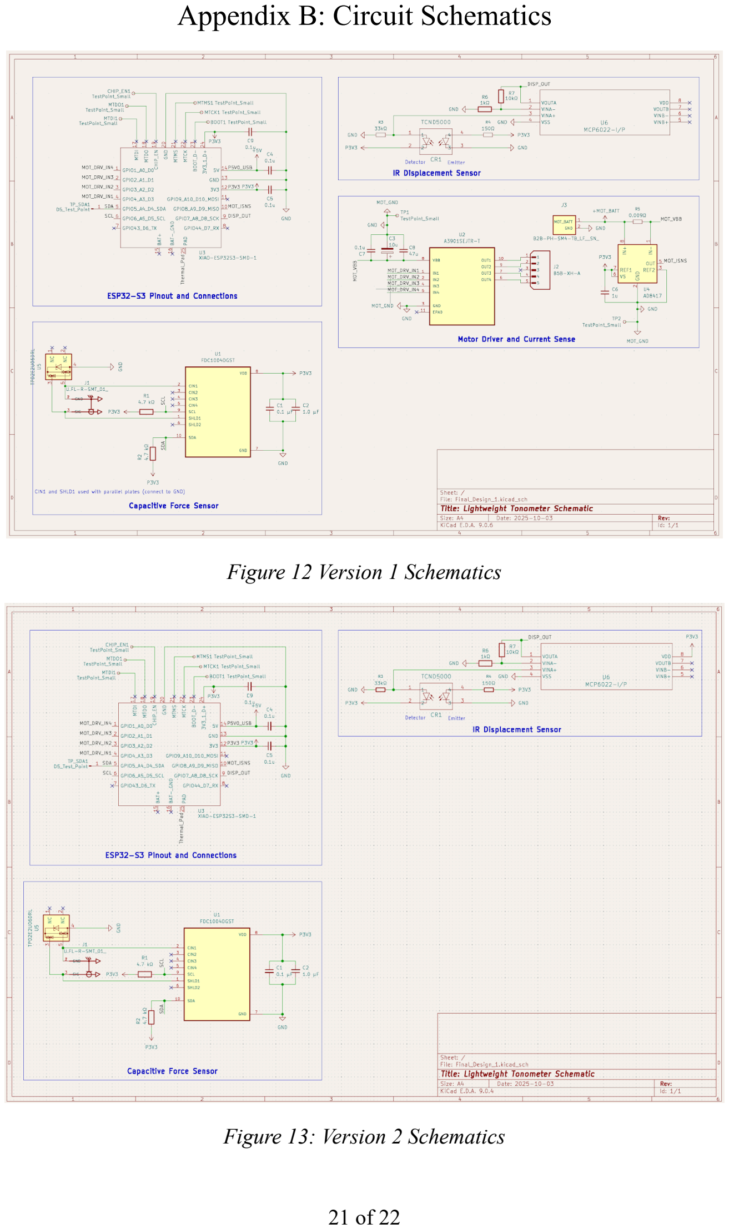
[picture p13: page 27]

Figure 12 Version 1 Schematics

Figure 13: Version 2 Schematics

### References

[1] Calzon, Maysen E, J. Blebea, and C. Pittman, “Quantitative measurement of pitting edema with a novel edema ruler,” Journal of Vascular Surgery Cases, Innovations and Techniques, vol.
10, | no. | 1, | 2024, | doi: | https://doi.org/10.1016/j.jvscit.2023.101373. | Available:
https://doi.org/10.1016/j.jvscit.2023.101373.
[2] Mayo Clinic, “Edema - symptoms and causes,” Mayo Clinic, Jul. 28, 2023. Available: https://www.mayoclinic.org/diseases-conditions/
[3] “Peripheral Arterial Tonometry: Non-Invasive Test for Vascular Health - The Kingsley
Clinic,” | The | Kingsley | Clinic, | 2025.
https://thekingsleyclinic.com/resources/peripheral-arterial-tonometry-non-invasive-test-for-vascular-health/ (accessed Dec. 03, 2025).
[4] K. Wolf-Cloud, “What are Technology Readiness Levels, and where is Wind Harvest in the process towards full commercialization of the first utility-scale H-type turbine?,” Wind Harvest,
Dec. | 01, | 2021.
https://windharvest.com/blog/faq-items/what-are-technology-readiness-levels-and-where-is-wind-harvest-in-the-process/
[5] Cleveland Clinic, “Edema: Causes, Symptoms & Treatment,” Cleveland Clinic, May 17, 2022. https://my.clevelandclinic.org/health/diseases/12564-edema (accessed Dec. 03, 2025).
[6] T. Bieze, F. Largillière, and S. Hage Chehade, “FeTCh Mark 1 Manipulator | Soft Robotics
Toolkit,” Soft Robotics Toolkit, 2015. https://softroboticstoolkit.com/fetch (accessed Dec. 03, 2025).
[7] Jutamanee Auysakul, Apidet Booranawong, Nitipan Vittayaphadung, and Pruittikorn Smithmaitrie, “An Optimized Design of the Soft Bellow Actuator Based on the Box–Behnken Response Surface Design,” Actuators, vol. 12, no. 7, pp. 300–300, Jul. 2023, doi: https://doi.org/10.3390/act12070300.
[8] J. Su, K. Zuo, and Z. Chua, “Three Degree-of-Freedom Soft Continuum Kinesthetic Haptic Display for Telemanipulation Via Sensory Substitution at the Finger,” Research Gate, Sep. 17.
[9] Zeke and Zeke, “Industrial Silicone Hardness Guide: Choosing the Right Shore A for Your
Application,” | Custom | Silicone | Molding, | Jul. | 24, | 2025.
https://www.newtopcustomsilicone.com/industrial-silicone-hardness-guide-choosing-the-right-shore-a-for-your-application/

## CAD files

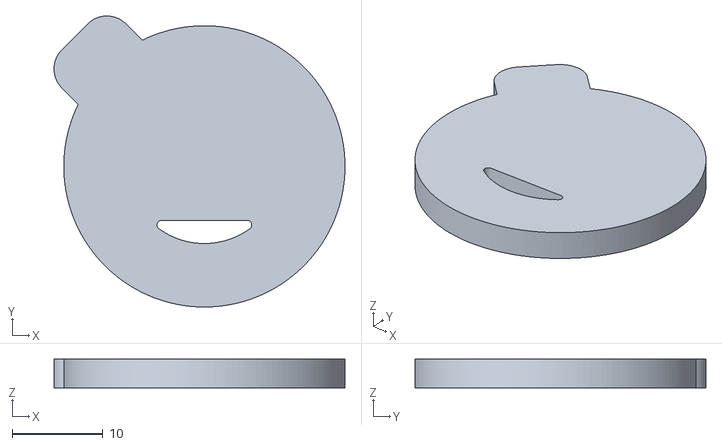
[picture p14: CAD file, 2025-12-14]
Air-Intake-Plate-Plus-Clear-Plate-Design/Clear Plate.stl
32.1 x 32.1 x 3.17

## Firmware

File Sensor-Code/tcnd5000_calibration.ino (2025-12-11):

// TCND5000 Calibration Script

// Define analog input pin connected to TCND5000 sensor
const int DISP_OUT = A8;

/* ---------------- Low-pass filter parameters ---------------- */

// Sampling period (in seconds). Here: 0.0001 s = 100 µs → 10 kHz sampling rate
float sample_period = 0.0001; 

// Desired cutoff frequency for the low-pass filter (Hz)
float cutOff_frequency = 2;

// Sampling rate derived from sample period
float sampling_rate = 1 / sample_period;

// Exponential smoothing factor for low-pass filter
// Formula: exp(-2π * fc / fs), where fc = cutoff frequency, fs = sampling rate
float smoothing_factor = expf(-2 * PI * cutOff_frequency / sampling_rate);

/* Stores the previous filtered value (initially 0) */
float filteredValue = 0;

void setup() {
  Serial.begin(115200);     // Initialize serial communication at 115200 baud
  pinMode(DISP_OUT, INPUT); // Configure sensor pin as input
}

// Main loop: reads sensor, applies filter, converts to displacement
void loop() {

  int samples = 50;       // Number of samples to average
  float total = 0.0;      // Accumulator for filtered values

  for (int i = 0; i < samples; i++) {

    /* Read raw analog data from TCND5000 sensor */
    float raw = analogRead(DISP_OUT);

    /* Apply exponential low-pass filter:
       filtered[k] = (1 - α)*raw + α*filtered[k-1]
       where α = smoothing_factor
    */
    filteredValue = (1.0f - smoothing_factor) * raw + smoothing_factor * filteredValue;
    
    /* Accumulate filtered samples */
    total += filteredValue;

    // Small delay to match sampling period (100 µs)
    delayMicroseconds(100);
  }

  /* Compute average of filtered samples */
  float average = total / samples; 

  /* Convert ADC reading to voltage (mV):
     - ADC resolution: 12-bit (0–4095)
     - Reference voltage: 3.3 V = 3300 mV
     Formula: (ADC_value / 4095) * 3300
  */
  float voltage_mV = (average / 4095.0) * 3300.0;

  /* Convert voltage to displacement (mm) using calibration equation:
     displacement = 227 - 0.973 * voltage_mV
     (linear mapping derived experimentally for TCND5000)
  */
  double displacement = 227 - 0.973 * voltage_mV;

  /* ---------------- Grading Scale ----------------
     Assign grade levels based on displacement thresholds
  */
  if (displacement < 2) {
      Serial.print("Grade level: 1, Displacement: ");
      Serial.println(displacement);
  }
  else if (displacement < 4) {
      Serial.print("Grade level: 2, Displacement: ");
      Serial.println(displacement);
  }
  else if (displacement < 6) {
      Serial.print("Grade level: 3, Displacement: ");
      Serial.println(displacement);
  }
  else if (displacement < 8) {
      Serial.print("Grade level: 4, Displacement: ");
      Serial.println(displacement);
  }

  /* Debug/marker output:
     Prints fixed values (-10, 10) followed by displacement
     Possibly used for plotting or calibration reference
  */
  Serial.print(-10);
  Serial.print(", ");
  Serial.print(10);
  Serial.print(", ");
  Serial.println(displacement, 2); // Print displacement with 2 decimal places
}

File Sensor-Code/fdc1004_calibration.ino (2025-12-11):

#include <Wire.h>       // Include I2C communication library
#include <FDC1004.h>    // Include library for FDC1004 capacitive sensor

/******************************************************************************************/

/*********** FDC1004 **********/

// Define I2C pins for XIAO ESP32S3 board
const int SDA_PIN = SDA;  // GPIO5 = SDA line
const int SCL_PIN = SCL;  // GPIO6 = SCL line

// Variables for implementing a digital low-pass Butterworth filter
float yk1 = 0; // Previous output sample y[k-1]
float xk1 = 0; // Previous input sample x[k-1]

// Filter coefficients (pre-computed for cutoff = 10 Hz, sampling = 100 Hz)
const float a = 0.72848950367272; 
const float b = 0.13575752481636; 

// Create FDC1004 object, set sampling rate to 100 Hz
FDC1004 fdc(FDC1004_100HZ);

void setup() {
  Serial.begin(115200); // Start serial communication at 115200 baud

  // Initialize I2C bus with defined pins
  Wire.begin(SDA_PIN, SCL_PIN);
  Wire.setClock(100000); // Set I2C clock speed to 100 kHz

  delay(50); // Small delay to stabilize communication

  // No explicit begin() for FDC1004 library; Wire initialization is sufficient
  Serial.println("FDC ready (Wire initialized).");
}

void loop() {
  // Read capacitance from channel CIN1
  // Returned value is in femtofarads (fF) as int32_t
  float c_fF = fdc.getCapacitance(0); // Channel 0 = CIN1

  // Convert femtofarads to picofarads (1 pF = 1000 fF)
  float pf = c_fF / 1000;

  // Apply digital low-pass filter:
  // y[k] = a*y[k-1] + b*x[k] + b*x[k-1]
  float yk_c = a * yk1 + b * pf + b * xk1;

  /* Example calibration reference:
     Contact detected around 11.4 pF
     Printing format: fixed values + filtered capacitance
  */
  Serial.print(9);          // Example constant (could be marker or ID)
  Serial.print(", ");
  Serial.print(11);         // Example constant (could be marker or ID)
  Serial.print(", ");
  Serial.println(yk_c, 2);  // Print filtered capacitance with 2 decimals

  // Update previous samples for next iteration
  xk1 = pf;   // Store current input
  yk1 = yk_c; // Store current output

  delay(10); // Delay ~10 ms → loop runs ~100 Hz
}
